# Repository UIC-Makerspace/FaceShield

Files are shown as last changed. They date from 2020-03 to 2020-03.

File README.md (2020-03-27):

# FaceShield
A laser cuttable face shield for healthcare workers facing shortages

The design is two simple pieces and doesn't use any additional materials (we have found shortages of elastic and tapes to be a problem). The top portion prevents splash over and was requested by our environmental health and safety office. The band is adjustable in size with four positions. It allows for wearing glasses, safety goggles, and masks. They are incredibly quick to make - 20 seconds or so per mask (laser cutter depending)

Version 3 incorporates feedback from hospital testing making the assembly far simpler and making everything more adjustable. 

----
To assemble:

Video instructions:

Assembly Instructions (https://www.youtube.com/watch?v=A-IHaJ__zD8 "Assembly Instructions ")

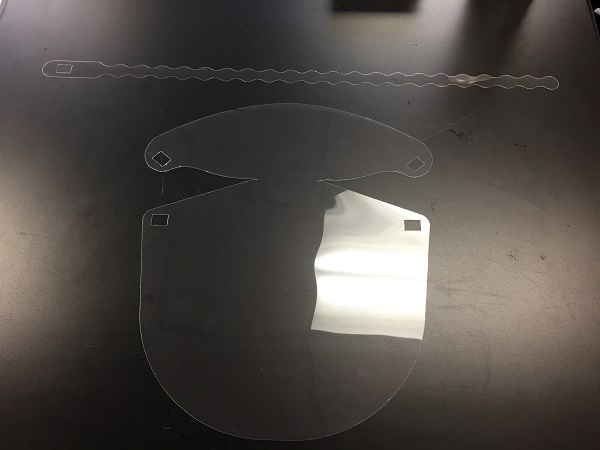
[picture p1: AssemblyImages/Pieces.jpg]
Pieces


1: Bring the rectangular cutouts together. 

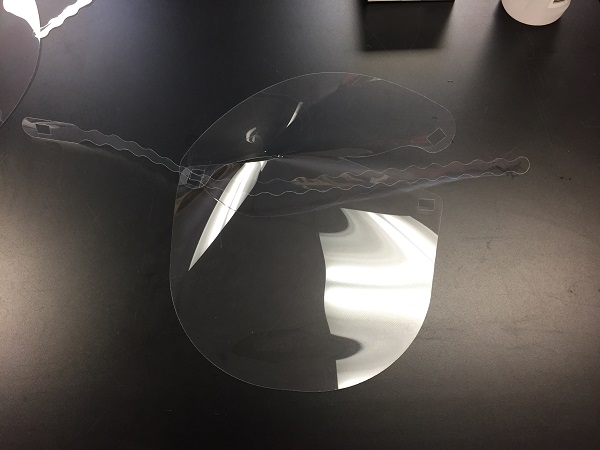
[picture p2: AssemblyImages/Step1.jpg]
Step 1


2: Thread the band through both rectangles. Repeat for other side. Recommended to keep the upper tabs to the outside of the shield.

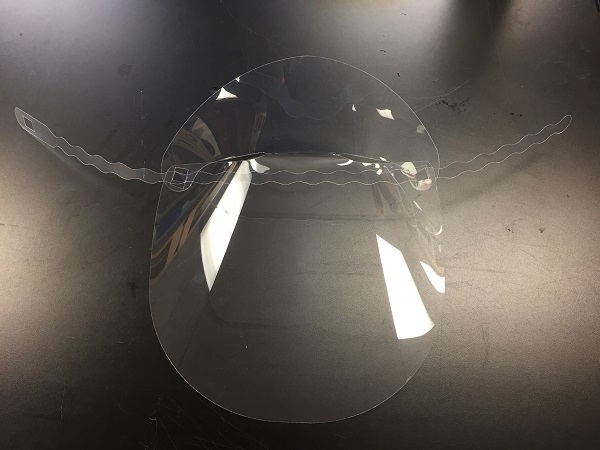
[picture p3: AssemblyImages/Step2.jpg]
Step 2


3: Put the shield on and slide the wavy part of the band through the rectangle to fasten the band. Adjust as necessary

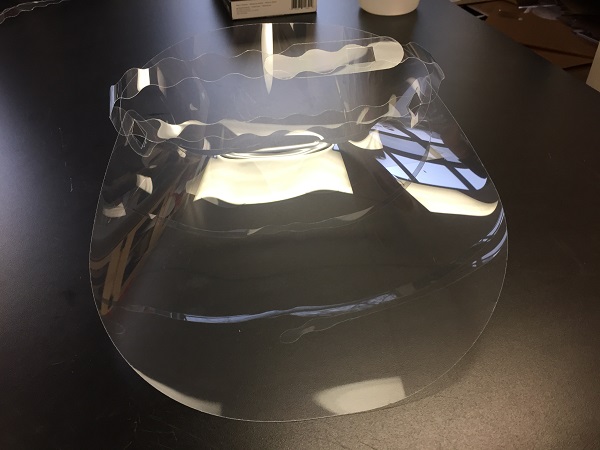
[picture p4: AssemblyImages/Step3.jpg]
Step 3


----
Material used is 0.005" PET. The design should accommodate other thicknesses of PET or even other materials. We also tested the design with 0.010" PET and 0.010" Cellulose Acetate. 

We have tested the materials with hospital sanitizers (1 cup : 1 gallon bleach; CaviWipes). Both PET and Cellulose Acetate have held up through many rounds of sanitation without adverse effects. 

The inspiration for this design came from: https://docs.google.com/document/d/1h6WlkQmBpClYxl8ALhX6QgyC4MXv_gm_8CsJsMSeZTI/edit

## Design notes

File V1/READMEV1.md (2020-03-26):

# FaceShield
A laser cuttable face shield for healthcare workers facing shortages

The design is two simple pieces and doesn't use any additional materials (we have found shortages of elastic and tapes to be a problem). The top portion prevents splash over and was requested by our environmental health and safety office. The band is adjustable in size with four positions. It allows for wearing glasses, safety goggles, and masks. They are incredibly quick to make - 20 seconds or so per mask (laser cutter depending)

----
To assemble:

Video instructions:

Assembly Instructions (http://www.youtube.com/watch?v=WwwImmXjGZU "Assembly Instructions ")

1: Lay the shield flat on a clean surface.

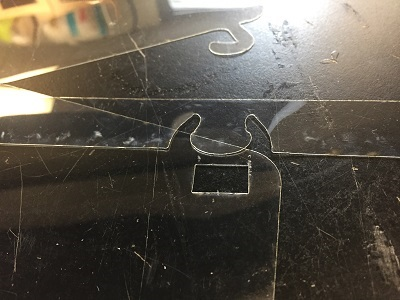
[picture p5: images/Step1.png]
Step 1


2: insert the tab on the band into the rectangle slot and pull taught.

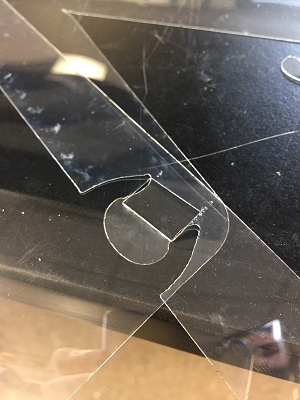
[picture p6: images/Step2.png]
Step 2


3: Pop the very bottom of the tab back towards you so the side flaps are on the opposite side of the shield from the band and the bottom flap is on the same side as the band. Think a Pringle or saddle shape.

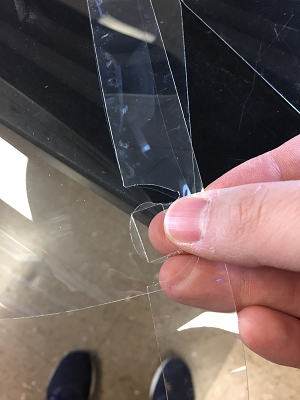
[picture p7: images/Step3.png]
Step 3

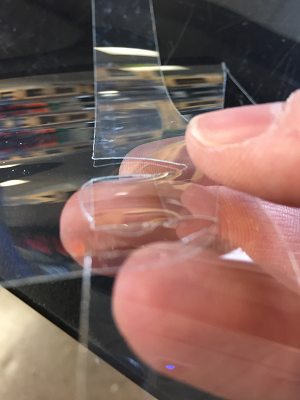
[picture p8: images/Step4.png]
Step 4


4: Hook the top splash shield into the band. The inside corners of the tabs work well but there are other options that can work depending on head shape. 

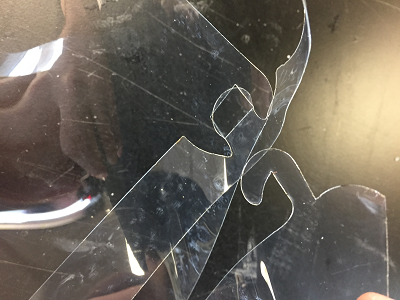
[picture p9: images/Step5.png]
Step 5

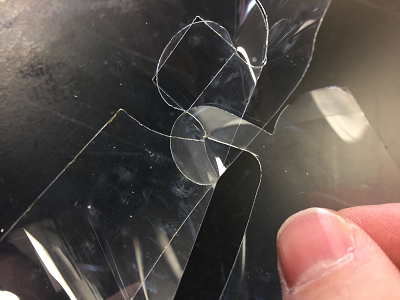
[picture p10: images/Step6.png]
Step 6


5: Put the shield on and slide the wavy part of the band through the rectangle to fasten the band. 

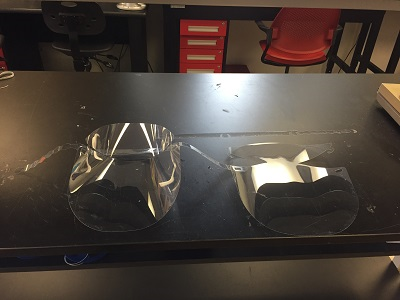
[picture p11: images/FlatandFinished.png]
Finished


----
Material used is 0.005" PET. The design should accommodate other thicknesses of PET or even other materials. We also tested the design with 0.010" PET and 0.010" Cellulose Acetate. 

We have tested the materials with hospital sanitizers (1 cup : 1 gallon bleach; CaviWipes). Both PET and Cellulose Acetate have held up through many rounds of sanitation without adverse effects. 

The inspiration for this design came from: https://docs.google.com/document/d/1h6WlkQmBpClYxl8ALhX6QgyC4MXv_gm_8CsJsMSeZTI/edit

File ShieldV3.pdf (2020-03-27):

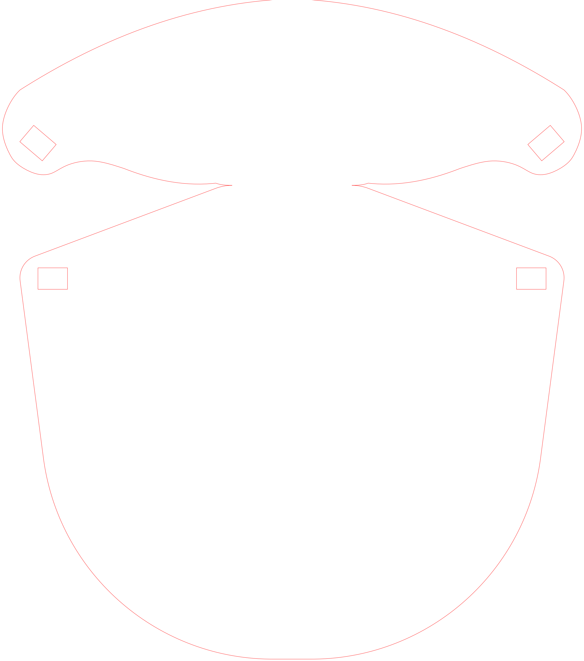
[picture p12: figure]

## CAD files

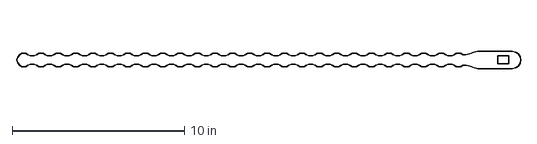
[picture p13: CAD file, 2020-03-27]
BandV3.dxf
29.3 x 1.00 in

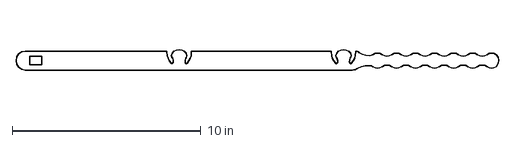
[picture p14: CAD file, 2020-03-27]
V1/Band.dxf
25.6 x 1.06 in

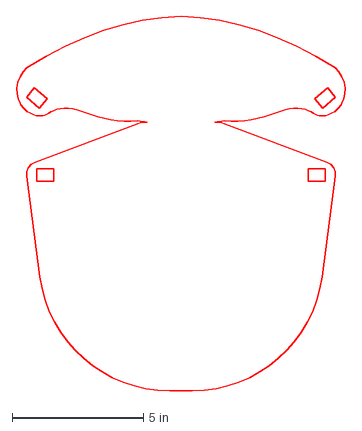
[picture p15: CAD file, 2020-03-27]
ShieldV3.dxf
12.6 x 14.3 in

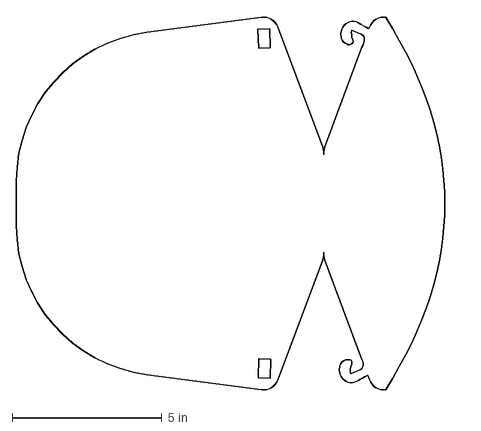
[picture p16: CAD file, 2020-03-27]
V1/Shield.dxf
14.9 x 12.5 in

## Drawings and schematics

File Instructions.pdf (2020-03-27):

### UIC Makerspace Face Shield Assembly Instructions Version 3

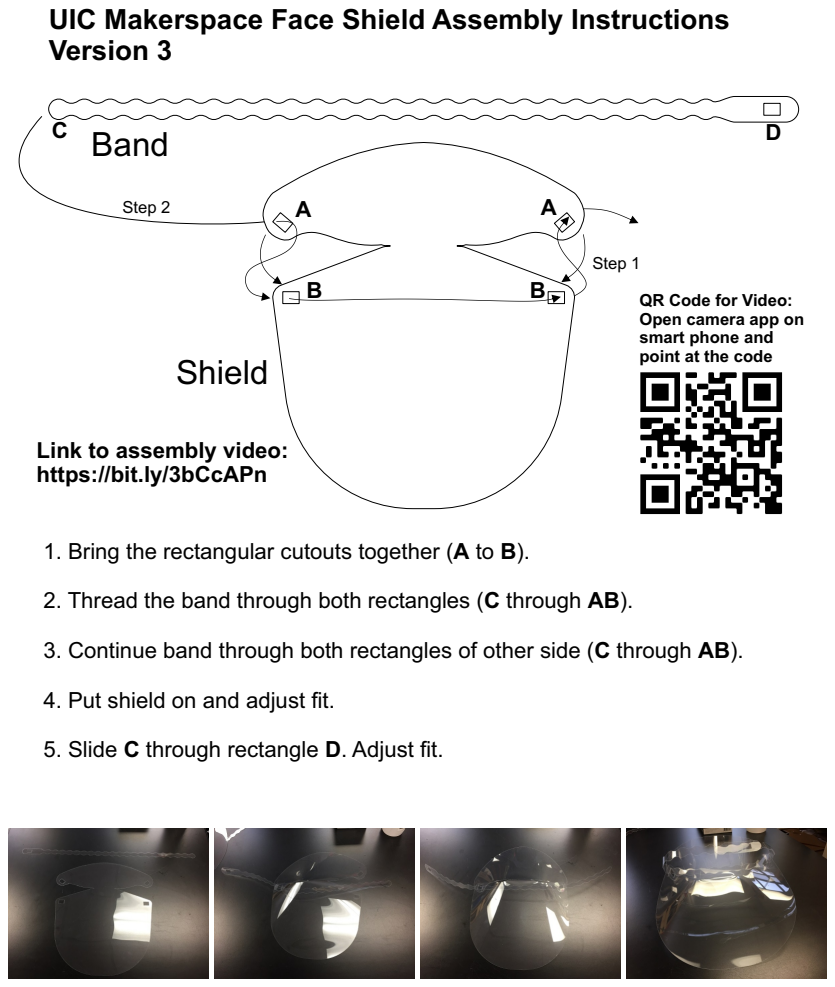
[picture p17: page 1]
Band; Shield; Step 1; Step 2

QR Code for Video:
Open camera app on
smart phone and
point at the code

Link to assembly video:
https://bit.ly/3bCcAPn

1. Bring the rectangular cutouts together (A to B).

2. Thread the band through both rectangles (C through AB).

3. Continue band through both rectangles of other side (C through AB).

4. Put shield on and adjust fit.

5. Slide C through rectangle D. Adjust fit.

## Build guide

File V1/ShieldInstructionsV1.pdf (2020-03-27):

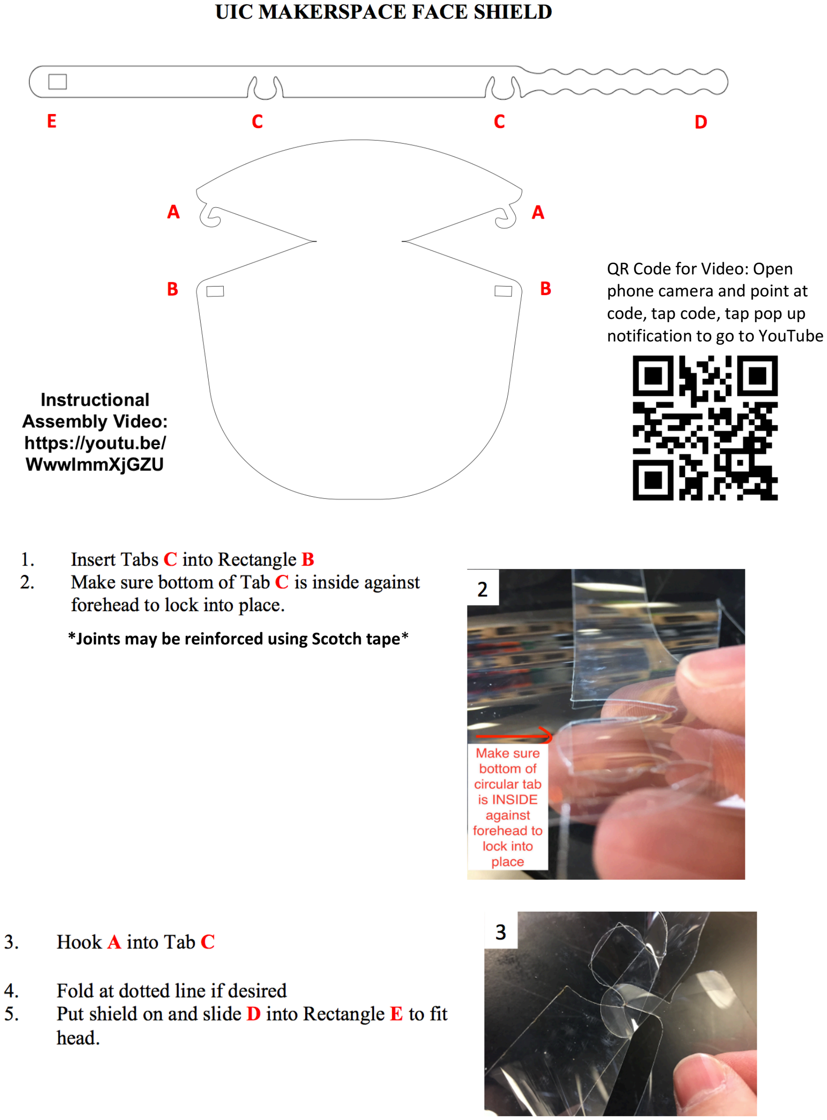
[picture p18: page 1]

QR Code for Video: Open
phone camera and point at
code, tap code, tap pop up notification to go to YouTube

*Joints may be reinforced using Scotch tape*

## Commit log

2020-03-24 Initial Upload
    These should be working files of various formats.
    [Band.dxf, Shield.dxf]
2020-03-27 Changed to version 3
    Version 3 (V2 was an incremental update) incorporates much feedback from the UIC Hospital users who are testing the design. Major changes are a decreased gap, much simpler assembly, and more adjustab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
    [Band.dxf, BandV3.dxf, Shield.dxf, ShieldV3.dxf]
2020-03-27 Assembly Instructions
